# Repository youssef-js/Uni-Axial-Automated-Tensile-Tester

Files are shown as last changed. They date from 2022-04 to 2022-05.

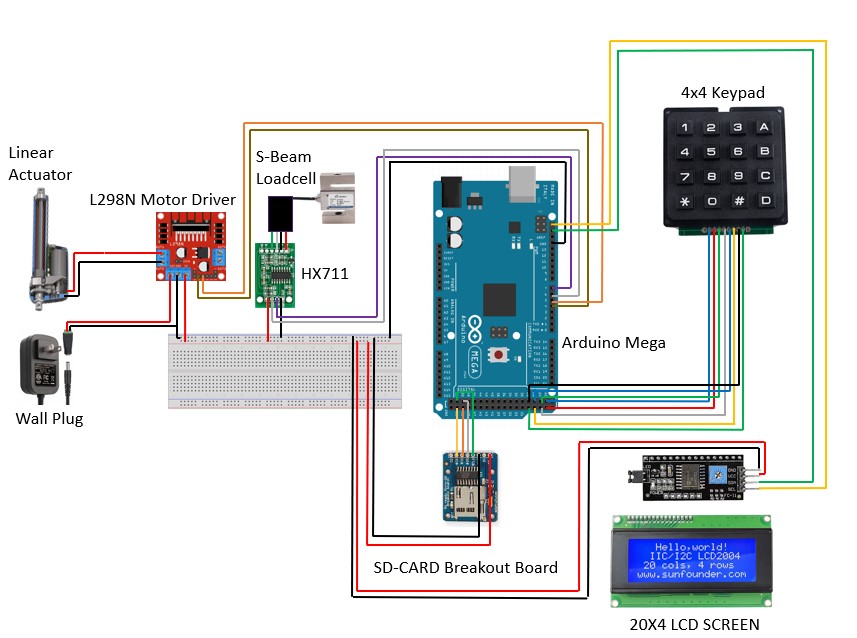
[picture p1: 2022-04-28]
Misc/Circuit Schematic.jpg

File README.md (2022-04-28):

# Uni-Axial Automated Tensile Tester
 ECE 442 Systems Analysis and Design Final Project
 
 The University at Albany’s chemistry department, as part of their educational mission, intends to build a laboratory for undergraduate students where they can gain hands on experience testing various material properties (including tensile strength).  However, due to the extremely high cost of commercial products they have been unable to equip such a laboratory.  

The goal of this project is to build an accurate, low cost, easy to use uniaxial tensile strength tester to support this educational mission. 

 ### Repository Contents
 
 In the interest of transparency all project reports have been included. Reading through this documentation will provide an individual with information on key milestones that were achieved during the progressive evolution of the product. Specifically the "Reports" folder contains the following: 
 
 * Logical Design Report
 * Physical Design Report
 * Experimental Results Report 

 Furthermore, within the "Presentations" folder viewers have been provided with a final copy of the poster displayed at the undergraduate research conference. As well as the presentation slides utilized within the classroom setting that exemplify the accomplished work within a condensed format.

 Lastly, in the scenario were an individual may wish to replicate the design we have provided the source code that is used to control the logic behind the device. Stl files have also been included, these can be found within the "Misc" folder. When printed the 3D models will yield the following:
 
 * Clamps
 * LCD Case
 * Keypad Case

Moreover, within the same folder will be a link to a webpage that will contain an appropriate training guide and more information on the apparatus.
 
  ### System Parts
  
  The system was designed with the intention of being completely reproducible by any individual with the desire to do so. As such for the convenience of the prospective designer, the utilized components and their respective links are compiled below:
  
  1. Drive System

     * Eco-Worthy 300mm Stroke Linear Actuator
  
       Link: https://www.amazon.com/dp/B00NM8H5SW?ref=ppx_yo2ov_dt_b_product_details&th=1
       
     * L298N Motor Driver
  
       Link: https://www.amazon.com/dp/B014KMHSW6?psc=1&ref=ppx_yo2ov_dt_b_product_details
      
     * Wall Mounted AC to DC Adapter
  
       Link: https://www.amazon.com/dp/B087NPBC1W?ref=ppx_yo2ov_dt_b_product_details&th=1
    
  2. User Interface
  
     * 20x4 LCD Display
  
       Link: https://www.amazon.com/dp/B08V4WB3Y1?ref=ppx_yo2ov_dt_b_product_details&th=1
       
     * 4x4 Matrix Keypad 
  
       Link: https://www.adafruit.com/product/3844?gclid=Cj0KCQjw06OTBhC_ARIsAAU1yOWN-53pa0KvsjR3zv9O0FhG5_UUUdQQNal-UVi3GDCMKE0uApMlhS8aAhVsEALw_wcB
      
     * Adafruit MicroSD Card Breakout Board
  
       Link: https://www.amazon.com/dp/B00NAY2NAI?psc=1&ref=ppx_yo2ov_dt_b_product_details
  
  3. Data Collection
  
     * HX711 Load Cell Amplifier
  
       Link: https://www.amazon.com/dp/B07MTYT95R?psc=1&ref=ppx_yo2ov_dt_b_product_details
       
     * S-type Beam High-Precision Load Cell
  
       Link: https://www.amazon.com/gp/product/B0785MXVYK/ref=ppx_yo_dt_b_asin_title_o00_s00?ie=UTF8&psc=1
       
     * Arduino Mega 
  
       Link: https://www.amazon.com/ELEGOO-ATmega2560-ATMEGA16U2-Projects-Compliant/dp/B01H4ZDYCE/ref=asc_df_B01H4ZLZLQ/?tag=hyprod20&linkCode=df0&hvadid=309743296044&hvpos=&hvnetw=g&hvrand=5459596528536033104&hvpone=&hvptwo=&hvqmt=&hvdev=c&hvdvcmdl=&hvlocint=&hvlocphy=9004731&hvtargid=pla-490931309987&th=1
       
  4. Store-Bought Components
  
     * Wood, Wood Screws, L Brackets, Magnets, Assorted Bolts/Nuts/Washers. 
  
       Store: Lowes
       
     * Load Cell Bolts
  
       Store: ACE Hardware

 ### Itemized Expenses
  
| Category      | Item          | Price |
| ------------- |:-------------:| -----:|
| Drive System  |Linear Actuator|$42.99 |
|               |L298N Driver   | $6.99 |
|               | AC-DC Adapter | $7.98 |
|               |               |       |
| User Interface| 20x4 LCD      | $6.33 |
|               | 4x4 Keypad    | $5.95 |
|               |MicroSD Board  | $9.56 |
|               |               |       |
|Data Collection|HX711 Amplifier| $1.99 |
|               |Load Cell      |$51.91 |
|               |               |       |
|Store-Bought   |All-Inclusive  |$30.00 |
|               |               |       |
|Grand Total    |-------------  |$163.70|

**Arduino Mega cost not included, the microcontroller was provided to the class by the instructor and therefore does not qualify as an expense.

   ### Software Dependencies
   
   In the context of software dependencies there is none for the traditional user. This apparatus requires no external downloads and is advertised as a complete stand-alone product due to the microSD functionality allowing for an individual to interact with data from the device in the form of a txt file. As such, appropriate data analysis can be performed at the users discretion, it is anticipated that for chemistry students excel will be the preferred tool.
   
However, when initially setting up the device one must upload the source code onto the microcontroller. The first step is to download the Arduino IDE, the appropriate link is found below:

Link: https://www.arduino.cc/en/software

Next, it is important that the required libraries for the provided Arduino source code are properly configured. The procedure for doing so is concisely formatted below:

   Utilize Link --> Press "Code" Button --> Download the ZIP --> Extract files into the "libraries" folder for Arduino.

   -HX711_ADC Library
   
   Link: https://github.com/olkal/HX711_ADC
   
   -LiquidCrystal_I2C Library
  
   Link: https://github.com/johnrickman/LiquidCrystal_I2C
   
   -Keypad Library
  
   Link: https://github.com/Chris--A/Keypad
   
   -EEPROM Library
  
   Link: N/A (Built into Arduino IDE)
   
   -Wire Library
  
   Link: N/A (Built into Arduino IDE)
   
   -SD and SPI Library
  
   Link: N/A (Built into Arduino IDE)

Syntax to reference libraries:

(Provided for the readers understanding, these lines of code have already been included within the source code and there is no need for the user to make any additions.)
```C
// Load cell
#include <HX711_ADC.h>
#include <EEPROM.h>

// LCD
#include <Wire.h>
#include <LiquidCrystal_I2C.h>

// Keypad
#include <Keypad.h>

// SD Card
#include <SD.h>
#include <SPI.h>
```

At this stage the setup in terms of software has been completed. Please download the source code provided within this repository and upload to the microcontroller to begin using the apparatus.

### Personnel and Funding

This project is completely funded by the Center For Undergraduate Research And Creative Engagement (CURCE). The designers applied for a $500 award and were subsequently granted the sum after passing the validation process. 

Designers

1. Youssef Jalwaj Soubai

2. Mazin Chater

3. Jaden Pharoah

Faculty Mentors/Support

1. Jonathan Muckell

2. Mike Denmark

Special thanks to Professor Chen, Feldblyun, Yeung, and the University at Albany’s Chemistry Department for sponsoring this project. 

Developed in ECE442: Systems Analysis & Design in the Electrical & Computer Engineering Department.

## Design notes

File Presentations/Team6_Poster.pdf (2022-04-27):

# Uni-Axial Automated Tensile System

# Youssef Jalwaj Soubai, Mazin Chater, Jaden Pharoah

## Department of Electrical & Computer Engineering, University at Albany

## Problem Statement

- The University at Albany’s chemistry department, as part of their educational mission, intends to build a laboratory for undergraduate students where they can gain hands on experience testing various material properties (including tensile strength). However, due to the extremely high cost of commercial products they have been unable to equip such a laboratory.
- The goal of this project is to build an accurate, low cost, easy to use uniaxial tensile strength tester to support this educational mission.

## System Requirements

## Experimental Results

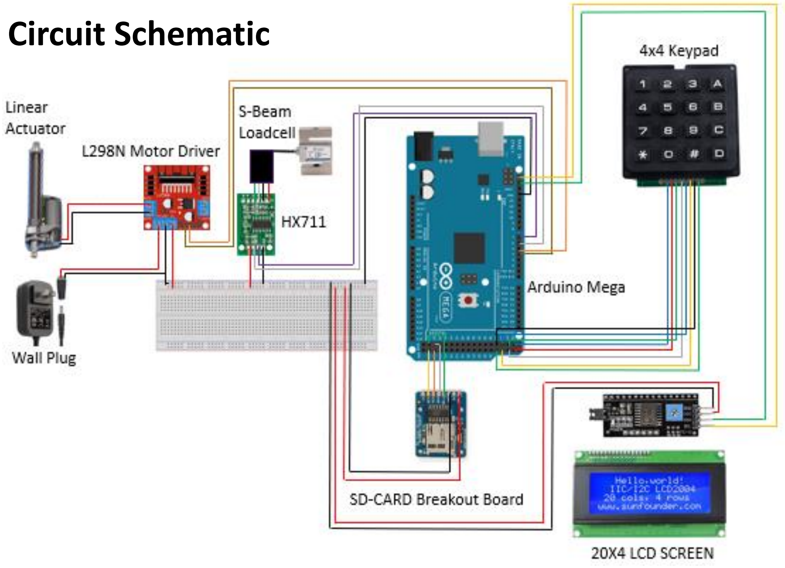
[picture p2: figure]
Circuit Schematic

## Project Partners

## System Design

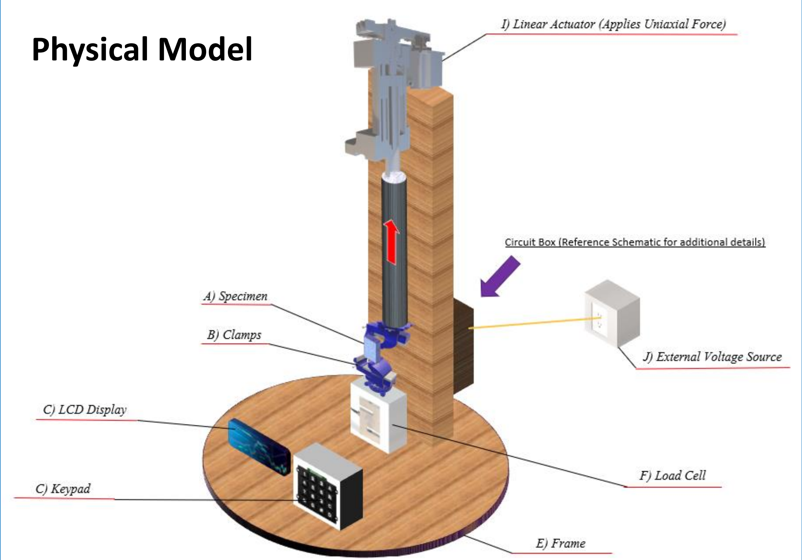
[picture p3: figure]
Physical Model

## System Enhancement Budget

Metric | Sample | Our System | Known Value
Young’s Modulus | Latex | 770 ± 30 kPa | 740 ± 10 kPa
… | Nitrile | 2.4 ± 0.2 MPa | 2.4 ± 0.2 MPa
Ult. Tensile Strength | Latex | 2.7 ± 0.3 MPa | 3.3 ± 0.1 MPa
… | Nitrile | 4.4 ± 0.4 MPa | 4.4 ± 0.1 MPa
Part | Purpose | Cost
50kg Load Cell | Measures Force | $50
Actuator System | Provides uniaxial force | $60
LCD, Keypad, SD | For stand-alone system | $30
Clamp Hardware | Combine 3-D printed parts | $10
TOTAL | | $150

## System Accuracy

- System Accuracy: The system should be able to accurately measure the stress-strain curve, such that Young’s Modulus and Ultimate Tensile Strength can be calculated to within two significant figures.
- System Ease-of-Use: The system should be easy to calibrate and operate by undergraduate students without requiring knowledge of electronics or software programming.

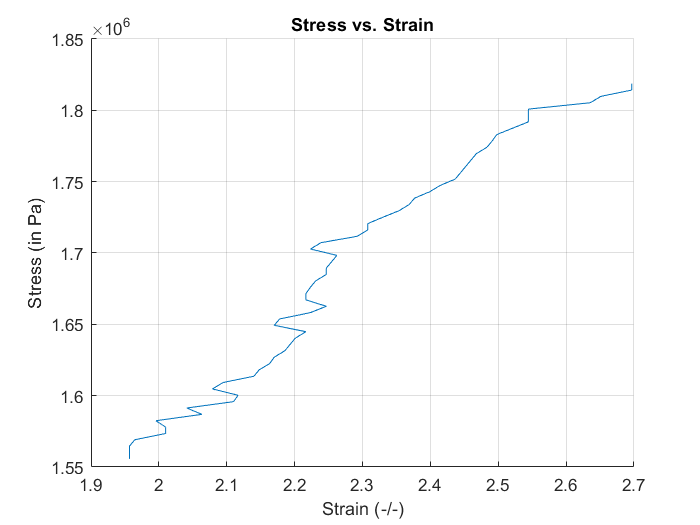
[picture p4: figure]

Figure 1: Original system data. The plot is filled with erroneous content.

## Key System Features

- Uniaxial Drive System - Composed of a L298N DC Motor Driver Module and an Eco-Worthy 300mm Stroke Linear
Actuator. Eliminates the risk of erroneous data due to friction.
- Stand-Alone Apparatus - The incorporation of an LCD screen, keypad, SD card capability and wall plug functionality allows for an independent system. Users can communicate with the device without any added software, thereby emphasizing the practicality of the device.
- Special thanks for Professor Chen, Feldblyun, Yeung, and the University at Albany’s Chemistry Department for sponsoring this project.
- This project was developed in ECE442: Systems Analysis & Design in the Electrical & Computer Engineering Department.

## Signature

## Initial vs. Current Stress/Strain Curves

# Team 6

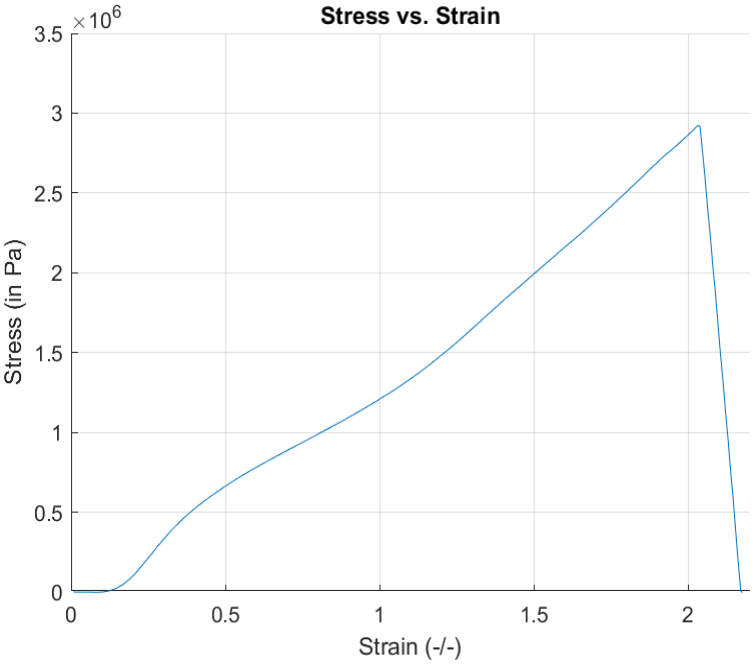
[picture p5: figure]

Figure 2: Data collected from improved system (current implementation). The plot is significantly improved, highlighting the importance of a drive system that applies uniform force.

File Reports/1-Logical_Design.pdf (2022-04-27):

PP-2017 V2.1

ANALYSIS & LOGICAL DESIGN | 1

# Logical Design Proposal Improved Tensile Tester Team 6

Mazin Chater, Youssef Jalwaj-Soubai, Jaden Pharoah

Activity Report

Abstract—A uni-axial tensile tester is a widely used system for gathering ultimate tensile strength and Young’s Modulus of a given material. Generally, these systems can be expensive and sophisticated yet their value as an educational tool for chemistry students is significant. As such, a cheaper, student-friendly design is highly desirable. Provided a minimally functional base model with issues ranging from largely inaccurate and imprecise results, obscure functionality, and generally an unpleasant and non-intuitive user interface, a targeted solution must aim to re-envision and harmonize the old structure into a more refined prototype. What follows is an advanced design that rectifies a number of defects as well as markedly improves accuracy and reliability. Additional ease-of-use features are implemented with an emphasis towards student use. The new capabilities deliver a low-budget, discernibly innovative solution with supporting documentation that sum to provide an accessible educational tool for students.

Index Terms—Uniaxial Tensiometer, System Analysis, Engineering Design

✦

### 1 BACKGROUND

T
ENSILE testers are instruments crucial in the study of materials science. A vast majority of those on the market, however, are thousands of dollars for a single unit and can be overly sophisticated beyond the scope of educational benefit. An alternative solution has been designed with these limitations in mind – one that is fundamentally simplistic with student use considered at its core [1]. The existing solution, nevertheless, has extensive flaws that hinder at the overall goals of reliability, accuracy, and accessibility. Most prominently, the accuracy of the system is only within an order of magnitude of accepted values which is due to a variety of factors including friction losses and unnecessary parts which add
- Mazin Chater,
E-mail: mchater3@albany.edu,
- Youssef Jalwaj-Soubai,
E-mail: yjalwaj-soubai@albany.edu,
- Jaden Pharoah,
E-mail: jpharoah@albany.edu, University at Albany.

to erroneous load cell readings. Ease-of-use is also obstructed with the provided plastic clamps which are especially time-consuming and inconsistent when holding materials. Likewise, data transfer must be performed manually from an Arduino interface to a MATLAB file to generate a stress-strain curve, creating a troublesome barrier for prospective chemistry students. In the purest sense, the following design resolves these issues by bridging the gap between a thought experiment and a fullyfunctional system.

### 2 SYSTEM REQUIREMENTS & CON-

STRAINTS

It’s important to define functional requirements of the system as outlined by both stakeholders and end users. At the forefront of the design must be accuracy and reliability. Having accurate results is only as useful as their consistency and having precisely inaccurate results is similarly of little utility. The constructed design aims to minimize error as well as to

Activity Report

2 | ANALYSIS & LOGICAL DESIGN

maximize reproducible trials. Another key aspect lies in the accessibility of the system. A
functional model is only worthwhile to those
who are capable its operation; therefore, there is merit in recognizing that additional software requirements, a non-intuitive structure and an intimidating arrangement of circuitry among other things are undesirable features to be mitigated. The following requirements describe functionality from a user’s perspective in ideal and alternative scenarios.

### 2.1 Accuracy and Precision

Accuracy is the characteristic that defines the adherence of a measure to a known value, whereas precision refers to the consistency of a measure across multiple iterations. Both qualities are integral to the stakeholder and a functional instrument must contain these attributes. Users engage with the apparatus to test a sample material. Interaction with the system must first consist of calibrating both the load and distance sensor. An LCD screen will guide the user through the process and prompt the participant to input appropriate values such as that of a sample mass or distance. Utilizing this data the sensors will be configured accordingly as to eliminate erroneous outputs. Furthermore, in order to ensure the quality of the load sensor data a more sophisticated load cell has been implemented to maximize the accuracy of measurements. In contrast, the current range sensor has proven to be dependable and is unlikely to be replaced.
Normal Flow
- Step #1: Initiate calibration process via button press.
- Step #2: Enter sample mass or distance value when prompted.
- Step #3: Instate the sample condition.
- Step #4: Confirm step via button press.
- Step #5: Repeat steps 2-4 until confirmation message is displayed.
- Step #6: Proceed with experiment. Alternative Flow This describes what will happen under an error condition.
- Step #1: Error message will display citing imprecise measurements.
- Step #2: User will be unable to proceed under erroneous conditions.
- Step #3: LCD Screen will prompt the user to initiate the calibration process once again.

### 2.2 Accessibility

Having an accurate and reliable system is significant, but the system must be functional for its intended audience. To make the system accessible, design elements shall consider the stakeholders’ experience and goals when interacting with the model and prioritize elements that maximize fluidity. An LCD screen in addition to its value as a calibration mechanism is also inherently user-friendly by providing simple options that hide the complex operations behind them. Users will merely select an option (i.e. start test, end test, send data, etc) and can disregard background intricacies. Modified clamps similarly serve to minimize setup time by dispensing with unnecessary screws and by implementing a simpler method whereby the clamps may open. Users will open each clamp with a single knob and firmly place the material in a matter of seconds, allowing for more tests to be conducted and minimizing hassle associated with the base model. Normal Flow
- Step #1: Place a sample firmly between both clamps.
- Step #2: Use the LCD screen to select the Start Test option.
- Step #3: Upon the sample tearing, select the End Test option.
- Step #4: Select the Send Data option.
- Step #5: Receive the data via network connection.
Alternative Flow This describes what will happen under an error condition.
- Step #1: Select the Refresh System option on the LCD screen.
- Step #2: Once reloaded, follow normal case steps.
- Step #3: If error persists, re-upload code using Arduino software as specified in the system documentation.

PP-2017 V2.1

SURNAME et al. | 3

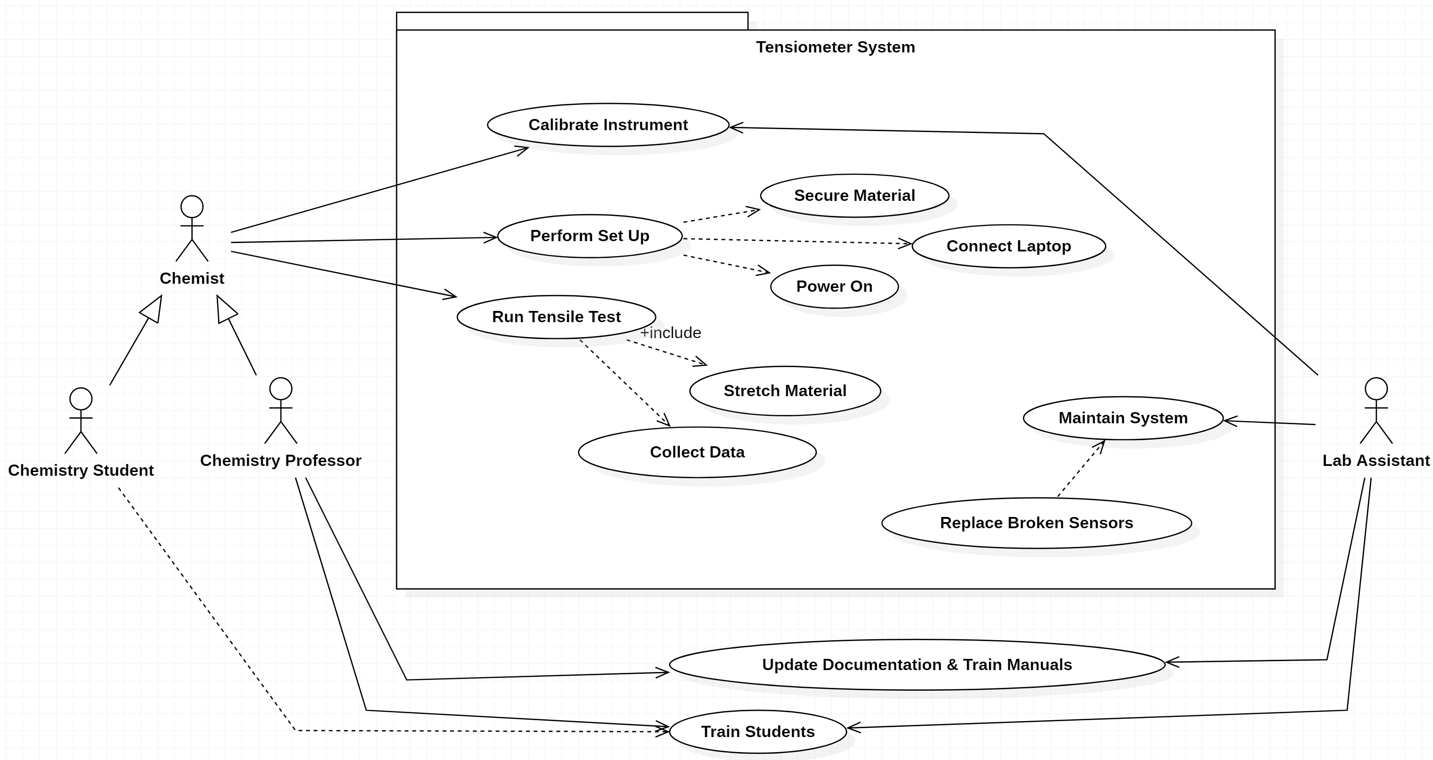
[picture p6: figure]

Figure 1. Use case model of the tensiometer system depicting system actors and the desired actions the system is required to support.

### 2.3 Constraints

The stakeholders have imposed certain restrictions upon the design process. System constraints are defined below and detail the conditions that the resulting testing apparatus must abide by.

- Time Constraint: Completed and ready to presentation/demonstrate by April 22nd
- Budget: Cost needs to be below $150. Exceeding the budget will require strong justification as to the value added from the cost overrun.
- Replication: Relatively straight-forward process to replicate project work, such that an individual can build out a lab of identical tensiometers.
- Accessibility of Parts: Parts need to be readily accessible, ship quickly (not on back order) and available from common part suppliers (e.g., Digikey, Mouser, Adafruit, SparkFun, Amazon). Parts that are difficult to source should be avoided.
- Safety: System must be safe to operate without significant training or supervision

### 3 LOGICAL DESIGN

The proposed design is simplistic in nature and abides by all given constraints. A visual depiction of the logical design is detailed within Figure 2. Referencing this image an individual first takes notice of the structural frame. A combination of wood and metal rods the testing apparatus lies upon a sturdy foundation. The drive system is comprised of a linear actuator that applies the necessary uni-axial force. The bottom clamp is attached to the end of the actuator, whereas the top clamp is fastened to the load cell. Our specimen of interest will be placed between these entities. Data will be collected from both the load cell and range finder. This information will be read by the micro-controller, processed accordingly and sent to the LCD display. Furthermore, if the user desires they may export the test data to their personal machine via network connection.

### 3.1 Design Justification

The proposed design is superior to potential alternatives due to a myriad of factors. Specifically, the selected design is an entirely stand

Activity Report

4 | ANALYSIS & LOGICAL DESIGN

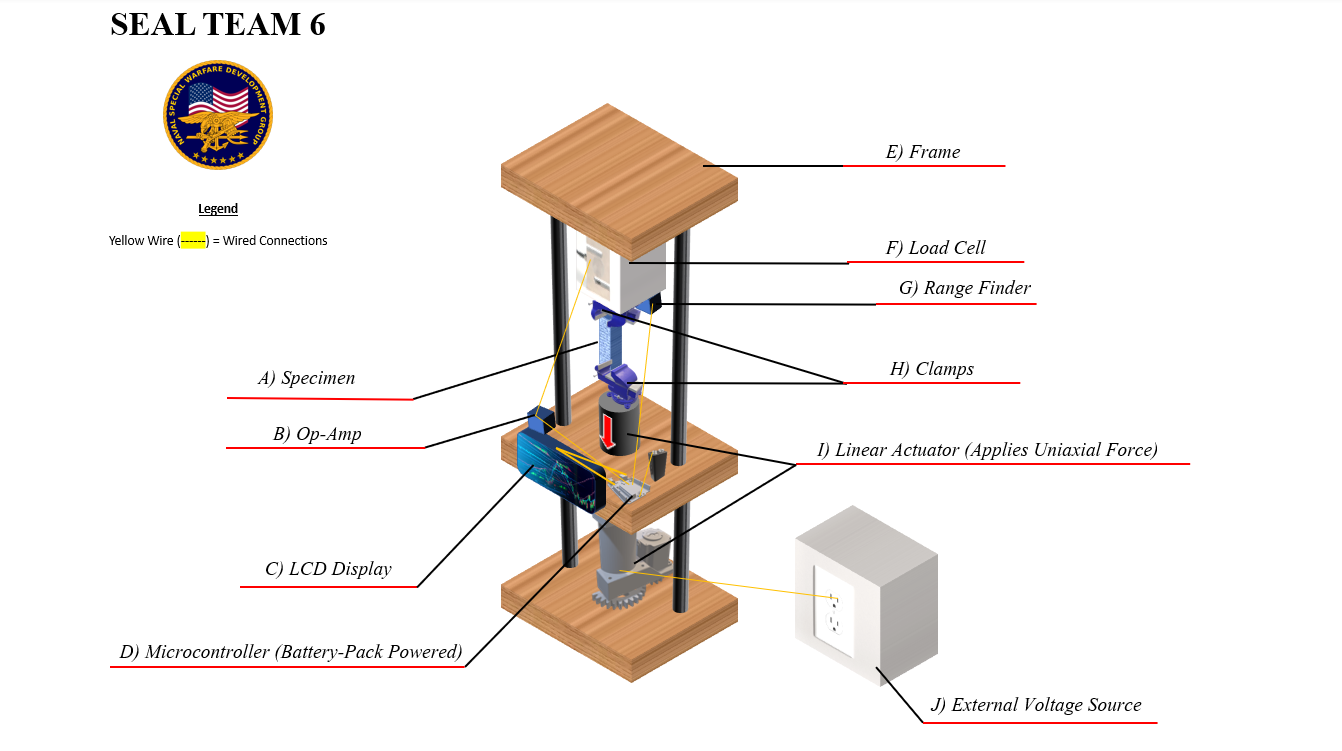
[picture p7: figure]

Figure 2. Logical prototype of the current system. Of key importance is the uni-directional movement of the clamps and addition of an interactive LCD screen as a user interface.

alone apparatus and does not require the user
to own a laptop. Removing such dependencies
denotes that all students will be able to participate within a lab regardless of preparation. Furthermore, the device is ergonomically sound, this denotes that even an individual with no prior experience may perform a successful tensile test. The entire process is iteratively walked through via clear instructions presented on the LCD screen. Moreover, the selected drive system allows for a constant and reliable form of force application. Utilizing the linear actuator a user will have far more consistent results compared to a manual system such as a handcrank. The referenced implementations sum to unveil a working mechanism that satisfies client requirements quite comfortably.

REFERENCES

[1] J. H. Arrizabalaga, A. D. Simmons, and M. U. Nollert, “Fabrication of an economical arduino-based uniaxial tensile tester,” Journal of Chemical Education, vol. 94, no. 4, pp. 530–533, 2017. [Online]. Available: https: //doi.org/10.1021/acs.jchemed.6b00639

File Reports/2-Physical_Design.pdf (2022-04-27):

PP-2017 V2.1

PHYSICAL DESIGN | 1

# Physical Design Proposal Seal Team 6

Mazin Chater, Youssef Jalwaj-Soubai, Jaden Pharoah

Activity Report

✦

### 1 PROPOSED SOLUTION

Targeting a significant increase in accuracy and precision along with an accessible architecture, the new system introduces a number of measured improvements. In terms of construction, a sophisticated yet simple clamp design is implemented along with a mounted S-beam load cell capable of greater flexibility in applied force as well as improved accuracy. A linear actuator applies uni-axial force to lift the top clamp upward, eliminating human error and providing uniform data collection. With accessibility in mind, an LCD screen guides users through the calibration and testing, minimizing barriers to entry otherwise prevalent with software. The features collectively combine under a new, custom frame designed for the aforementioned features.

### 2 SYSTEM ARCHITECTURE

A small wooden base holds the foundation for the system with a S-beam load cell being attached to the back center of the wood. Above, the carefully aligned bottom clamp attaches to the top of the load cell. The opposing clamp rests adjacent to the bottom clamp, effectively mirroring about the x-axis. When conducting

- Mazin Chater,
E-mail: mchater3@albany.edu,
- Youssef Jalwaj-Soubai,
E-mail: yjalwaj-soubai@albany.edu,
- Jaden Pharoah,
E-mail: jpharoah@albany.edu, University at Albany.

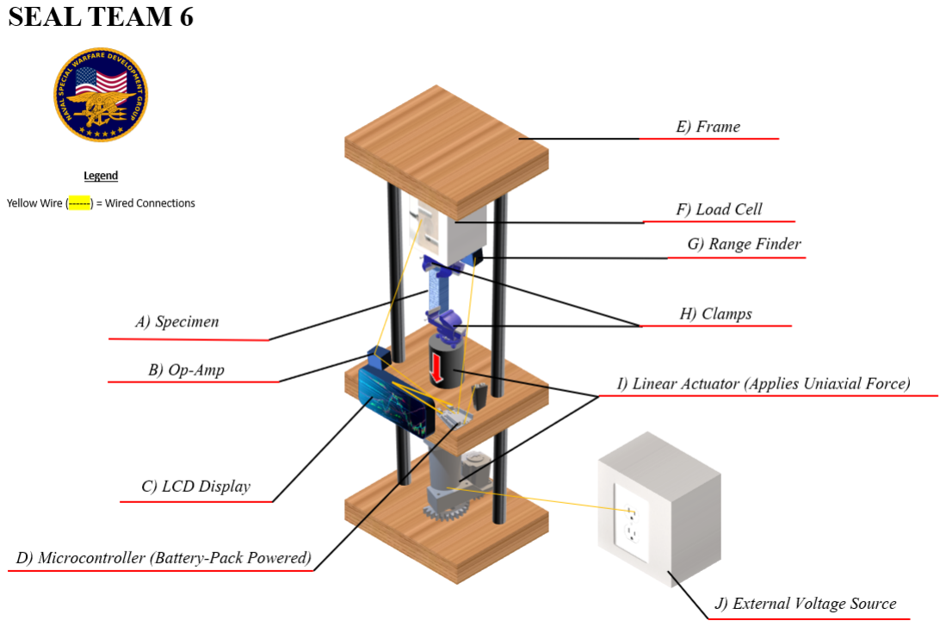
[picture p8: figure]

Figure 1. Prototype physical design model of the tensile strength tester with added features.

a test, the head of the top clamp is pulled upwards by a linear actuator that rests above. Back at the base, an LCD screen with trivial button inputs guides users through calibration, starting and ending tests, and sending collected data to a preferred destination.
A mounted breadboard and Arduino micro-controller connect to the load cell, distance sensor, and linear actuator. Specialized algorithms in a finite state machine are the basis for the design. As seen in Figure 2, the load cell becomes operational through connection to the HX711 board which uses the amplified value to perform a ADC conversion and then communicates the results using the I2C communication standard with the attached micro-controller. The load cell itself uses a wheatstone bridge to detect slight changes in voltage when an applied force is present. Additionally, the HC-SR04 distance sensor calculates distance with a trigger pin that sends a signal and an echo pin

Activity Report

2 | PHYSICAL DESIGN

which receives the signal. The time difference
along with the speed of sound is used to calculate distance. Furthermore, one must discuss
the nucleus of the design, a uniaxial drive system. The current working model incorporates the abilities of a ”L298N DC Motor Driver Module” and that of an ”Eco-Worthy 300mm Stroke Linear Actuator”. Including the L298N component allows for rotational direction control utilizing H-bridge properties. The motor driver also allows a user access to direction control pins that are easily interfaced with the Arduino micro-controller.

### 2.1 System Components

When considering the variety of materials to be tested in the prospective system especially those with higher ultimate tensile strengths, it became apparent that limiting exerted force to 5kg would be insufficient. It was also clear under the previous load-cell model that the application of force could only be done accurately in a precise, impractical environment. As such, a 50kg S-beam load cell has been implemented to vastly expand force possible while simultaneously maintaining accurate readings across extensive design elements. S-beam load cells vary in both cost and mass rating, though generally it should be noted that a number of these variants can be considered appropriate; 20kg, 40kg, and even 100kg are mass ratings that can be potentially utilized for distinct testing purposes. Observe, higher mass ratings yield higher inaccuracies in data readings and thus finding a balance between accuracy and capability should be evaluated.
User accessibility is another design criteria taken with consideration with the addition of an LCD screen interface. A 20x4 LCD screen guides users to navigate between testing phases such as running a test, calibration, and sending resultant data. A low cost LCD screen essentially gives users the ability to bypass complex software interfaces like the Arduino IDE and MATLAB. Rather than choose the somewhat more common 16x2 dimension, a 20x4 screen can print the entire menu concurrently without need for scrolling operations. An attached I2C board also simplifies wiring and congestion on the Arduino micro-controller. To interface with the screen, users interact with a linked membrane keypad implemented to register simple selections as well as recognizing a manual calibration input.
In the context of implementing a uniaxial drive system the available components on the market were rather limited due to the imposed budget cap. Ultimately the ”L298N DC Motor Driver Module” and ”Eco-Worthy 300mm Stroke Linear Actuator” were chosen due to their ease of use and affordability. Furthermore, a unique aspect of the L298N module is that it also powers the Arduino micro-controlller. As such, designers may advertise the final product as an entirely stand-alone system, this notion is a desirable quality that further emphasizes the ergonomic nature of the apparatus. Reference Figure 3 for an overview of incurred costs.

2.1.1 Load Cell (50kg) / HX711 Amplifier Functionality in the load cell effectively mirrors the previous model with enhanced precision, mass range, and accessibility in terms of mounting.

2.1.2 Ultrasonic Range Sensor
Preexisting in base model; see previous documentation.

2.1.3 Micro-controller
Preexisting in base model; see previous documentation.

2.1.4 Graphical Display
The new system gives users a membrane keypad to interact with a 20x4 LCD interface whereby navigation moves across four different states: menu, run test, calibration, and send data.

2.1.5 Uniaxial Drive System
Composed of a L298N DC Motor Driver Module and an Eco-Worthy 300mm Stroke Linear Actuator. The motor driver employs the use of an H-bridge to allow for direct control over rotational direction. Moreover users have access to input pins, this allows for seamless automation given an appropriate script.

PP-2017 V2.1

SURNAME et al. | 3

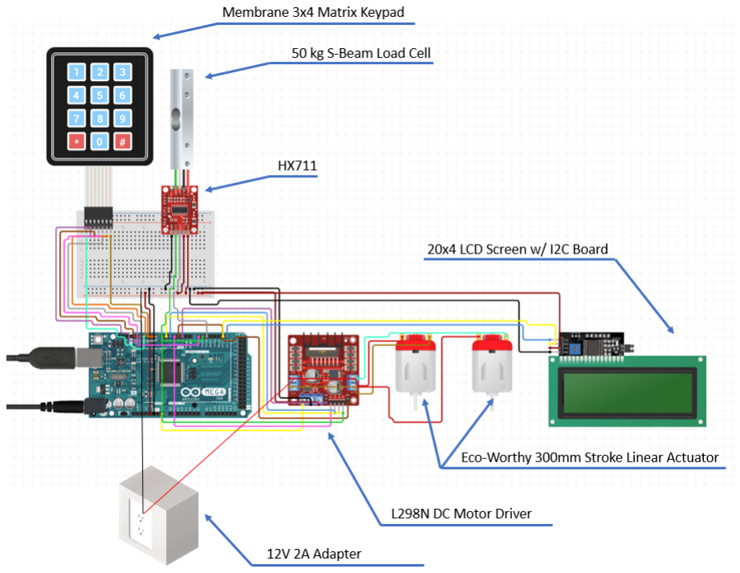
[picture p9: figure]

Figure 2. Schematic diagram of tensiometer electronics with additional actuator, LCD screen, and membrane keypad.

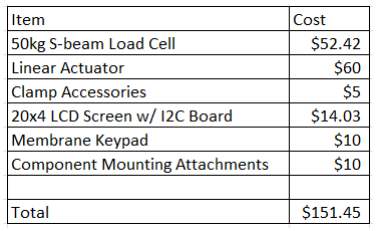
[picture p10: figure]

Figure 3. Parts purchased and their respective costs.

### 2.2 Engineering Standards

Engineering standards establish technical criteria, methods, processes and practices. In the current system, there are two communication standards (protocols) that are utilized: I2C and UART.

2.2.1 I2C Protocol
I2C supports multiple controllers and peripherals using just two wires (data and clock). In any new communication sequence, the address frame of 7 bits is always first followed by the ACK/NACK bit which gives confirmation that each frame is transferred successfully. Limited to 8 bits, the data frame begins transmitting data as the controller continues generating

Activity Report

4 | PHYSICAL DESIGN

clock pulses at a regular interval and the data
is placed on SDA by either the controller or
the peripheral. Once all the data frames have
been sent, the controller will generate a stop condition.

2.2.2 UART Protocol
UART ports communicate between only two devices (transmit and receive). Both devices must agree on data and communication speed ahead of time and requires complex hardware. There is no control over when the data is sent and no guarantee that both sides are running at the same rate. To achieve reduced data rates, at least one start and stop bit is a part of each frame of data.

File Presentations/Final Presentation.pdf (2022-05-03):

# Automated

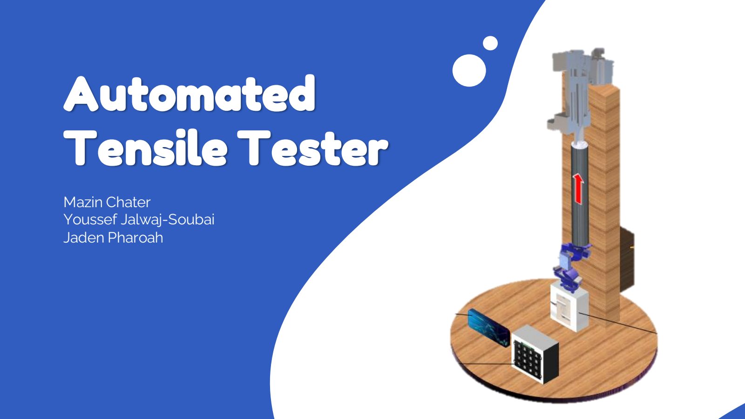
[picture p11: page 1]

# Tensile Tester

Mazin Chater
Youssef Jalwaj-Soubai
Jaden Pharoah

# Overview

Summary of system
functionality

## Abstract

How requirements
influenced the design

## System Features

Cost of individual
components

## Budget

A guide for prospective
users

## Website

Live test results &
discussion

## Data

Time to answer any
questions

Q/A

01

04

02

05

03

06

# Abstract

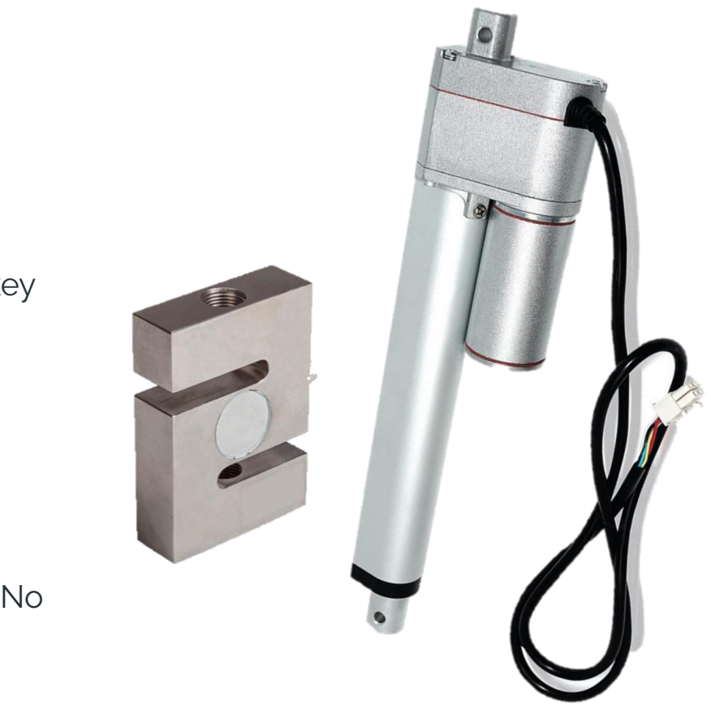
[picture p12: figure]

Our design revolves around these key design aspects:

- Linear actuator
- S-beam load cell
- LCD & keypad
- SD card

The system is entirely stand-alone. No software or laptop is required.

# System Requirements

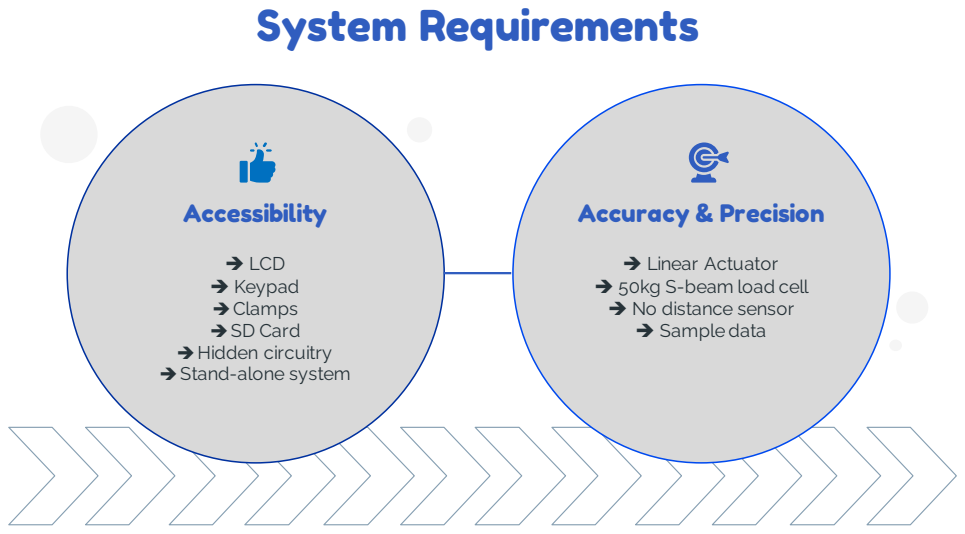
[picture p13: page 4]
Accessibility; Accuracy & Precision

➔ LCD
➔ Keypad
➔Clamps
➔SD Card
➔Hidden circuitry
➔Stand-alone system

➔ Linear Actuator
➔ 50kg S-beam load cell
➔ No distance sensor
➔ Sample data

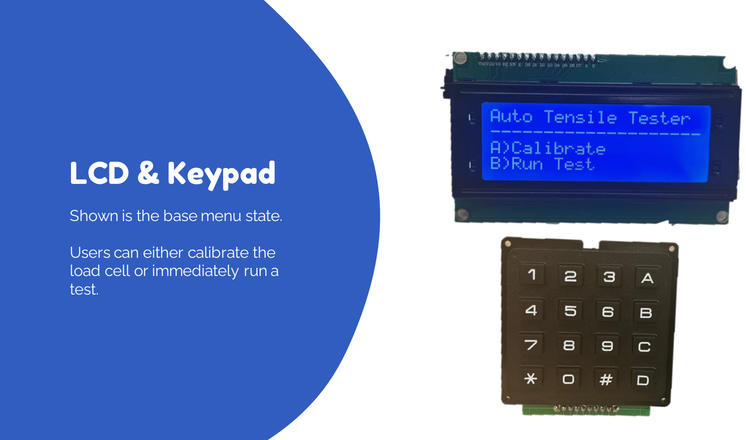
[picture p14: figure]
LCD & Keypad; Shown is the base menu state.; Users can either calibrate the load cell or immediately run a test.

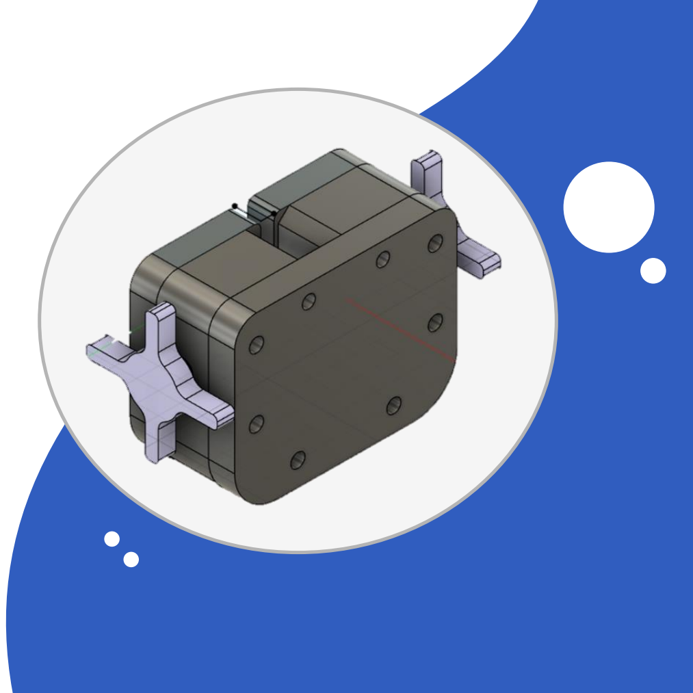
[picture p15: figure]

# Clamps

Strong grip clamps provide easy material placement and uniform sample strain.

Users mount the material in place and return to the LCD interface when ready.

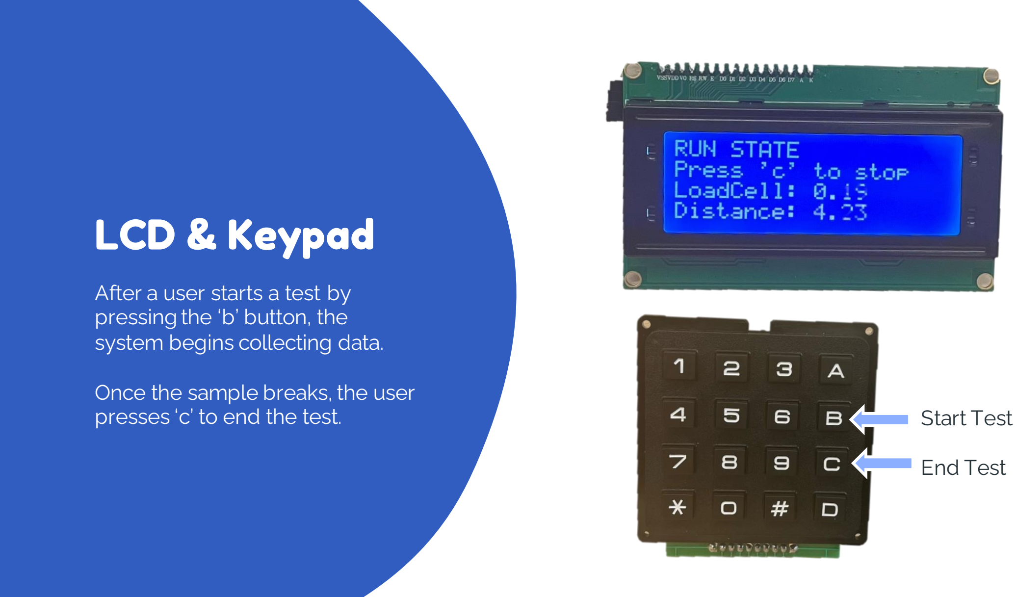
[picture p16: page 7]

# LCD & Keypad

After a user starts a test by pressing the ‘b’ button, the
system begins collecting data.

Once the sample breaks, the user
presses ‘c’ to end the test. | Start Test
| End Test

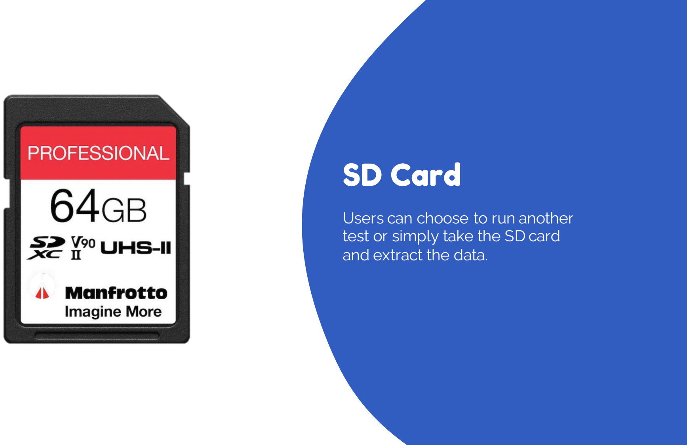
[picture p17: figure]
SD Card; Users can choose to run another test or simply take the SD card and extract the data.

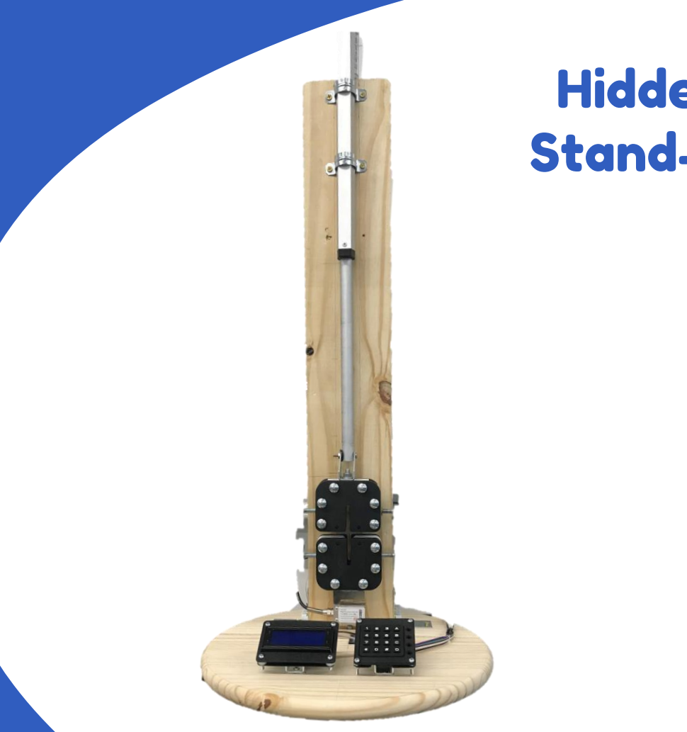
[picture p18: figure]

# Hidden Circuitry & Stand-Alone System

No specific software necessary. No laptop required.
→ Simply plug-in and start collecting data.

Essentially all wires are hidden on the backside of the system.

Users simply see the LCD and keypad interface along with the sample stretching.

# Accuracy & Precision

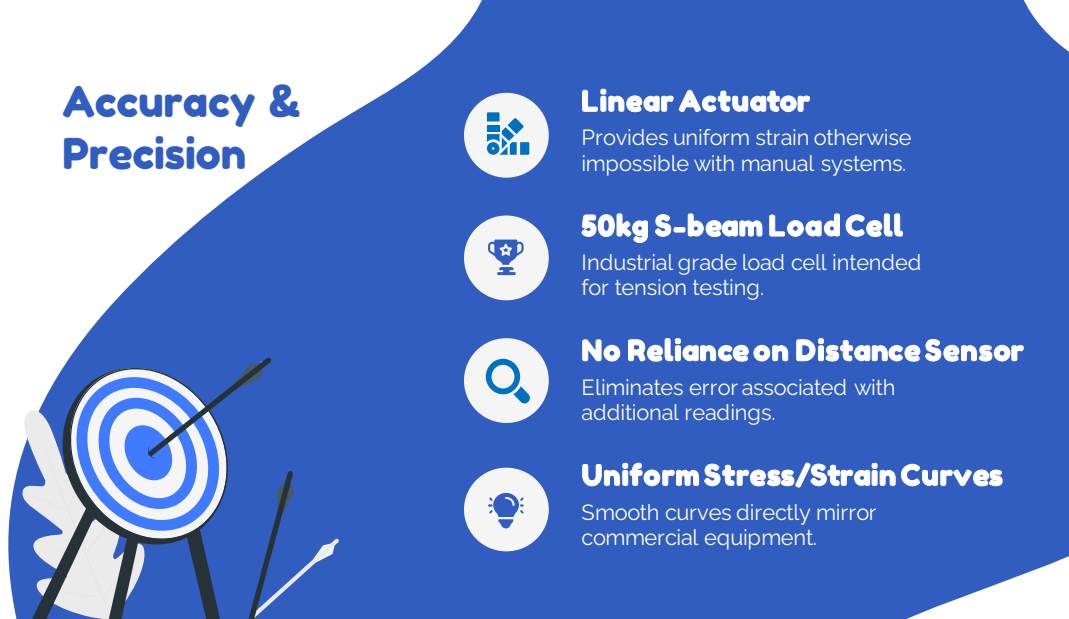
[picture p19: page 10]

Linear Actuator
Provides uniform strain otherwise
impossible with manual systems.
50kg S-beam Load Cell
Industrial grade load cell intended
for tension testing.
No Reliance on Distance Sensor
Eliminates error associated with
additional readings.
Uniform Stress/Strain Curves
Smooth curves directly mirror
commercial equipment.

# Sample Plots: Nitrile

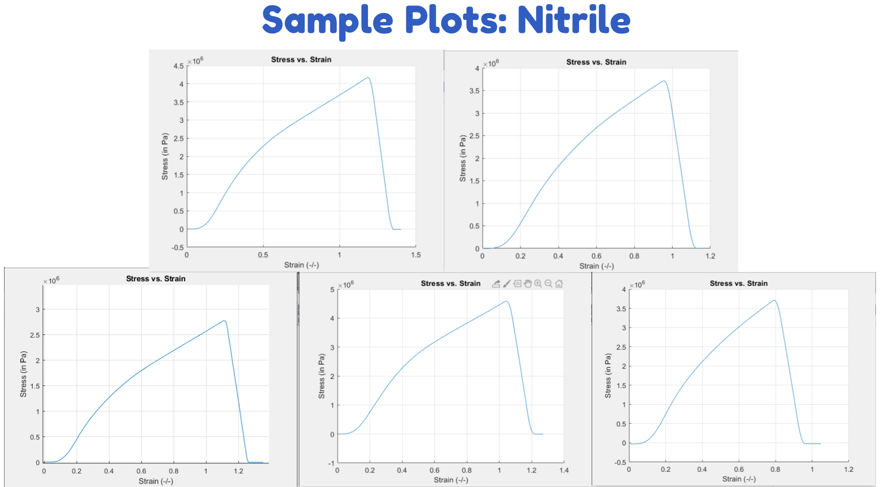
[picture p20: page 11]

# Sample Plots: Latex

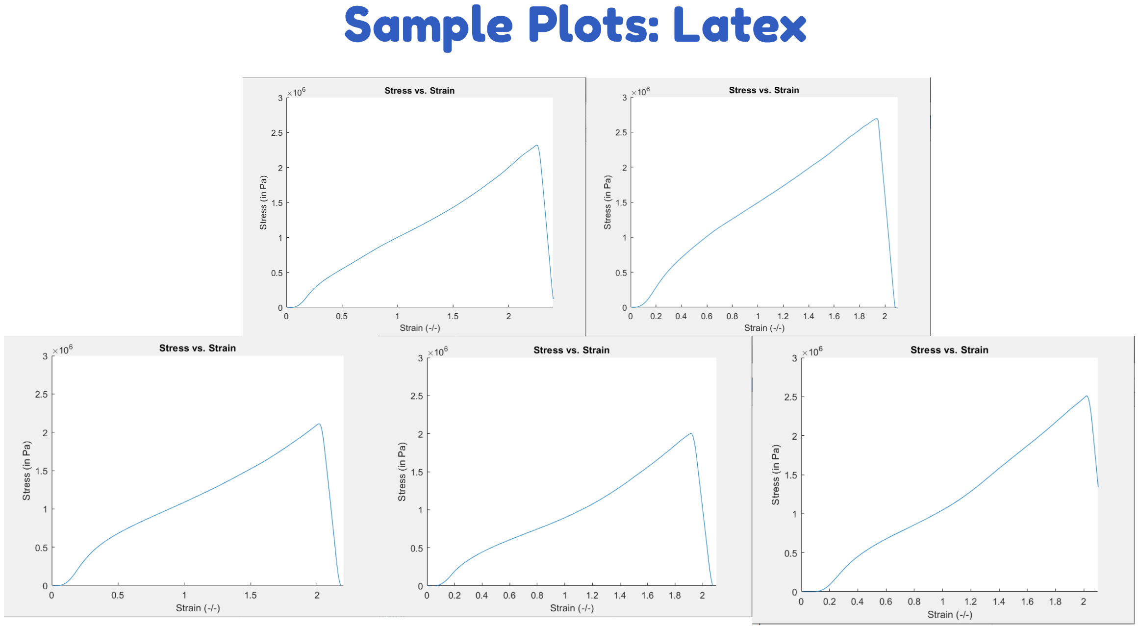
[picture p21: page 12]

# Budget

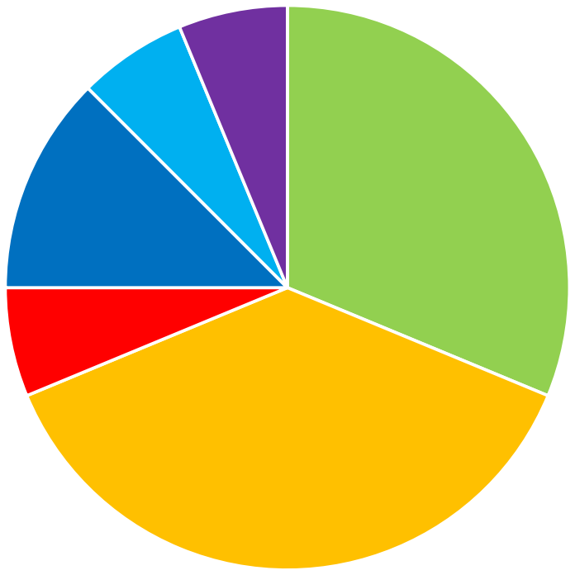
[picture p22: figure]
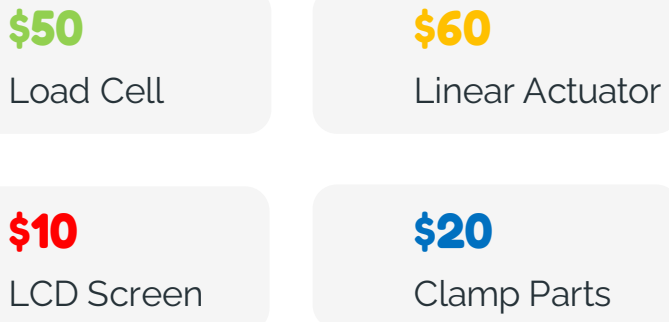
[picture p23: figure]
Clamp Parts; Linear Actuator; LCD Screen; Load Cell

Keypad

$10
SD Card

$10

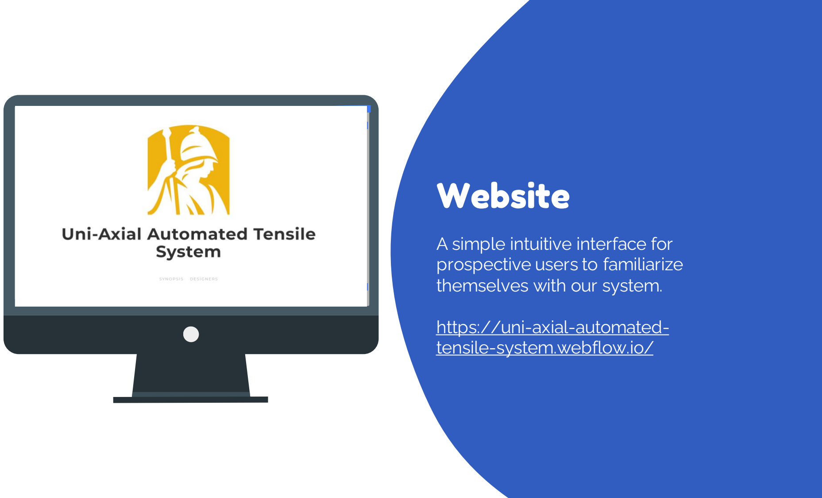
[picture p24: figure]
Website; A simple intuitive interface for prospective users to familiarize themselves with our system.; https://uni-axial-automated- tensile-system.webflow.io/; AUTOMATED TENSILE SYSTEM; Mazin Chater; Youssef Jalwaj Soubai; Jaden Pharoah

# Thank you

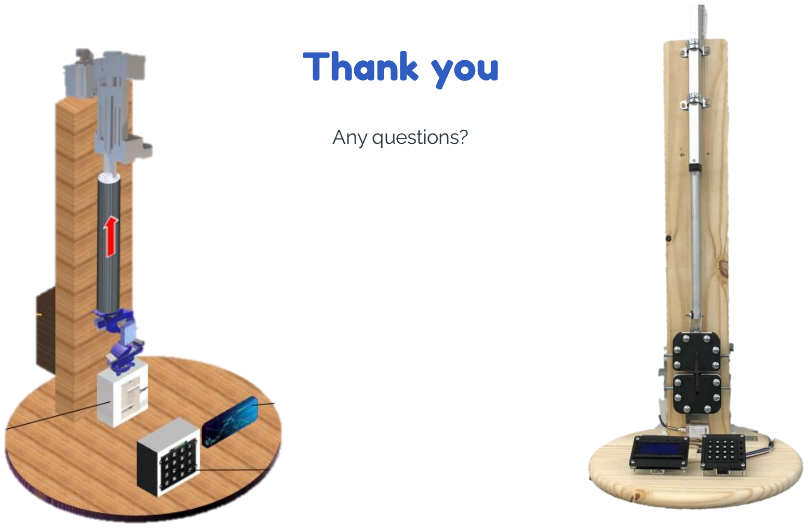
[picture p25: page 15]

Any questions?

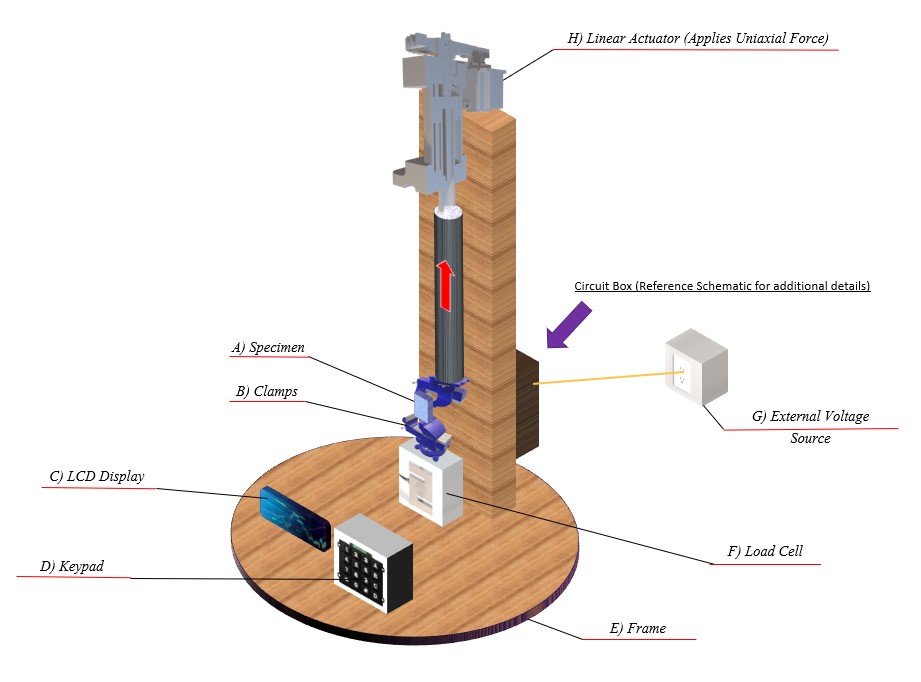
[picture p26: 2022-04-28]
Misc/Physical Model.jpg

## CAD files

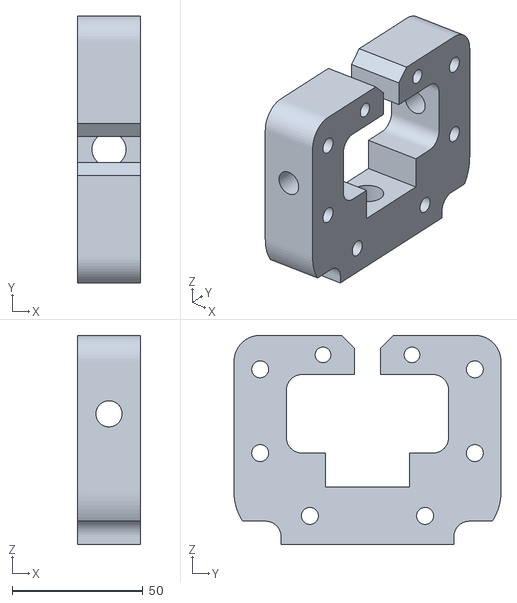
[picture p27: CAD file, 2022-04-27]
Misc/Clamp 3D Model/Central_Piece.stl
24.0 x 102.0 x 80.0

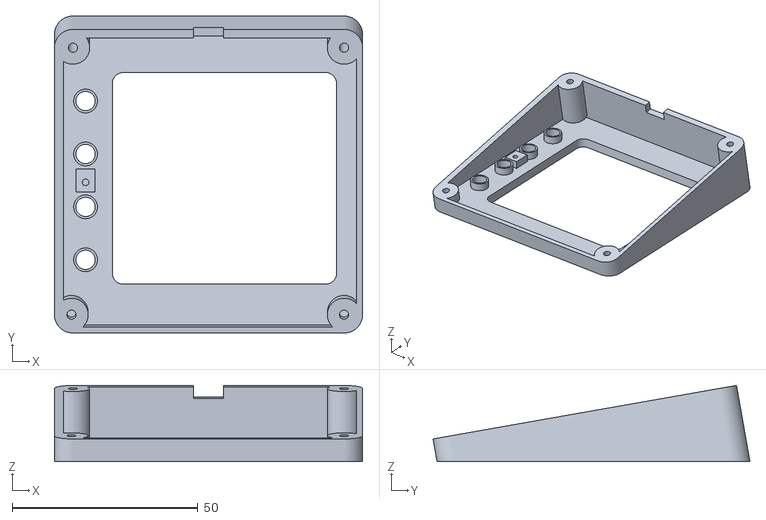
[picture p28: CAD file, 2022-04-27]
Misc/Keypad Case 3D Model/case-top.stl
83.0 x 85.4 x 20.5

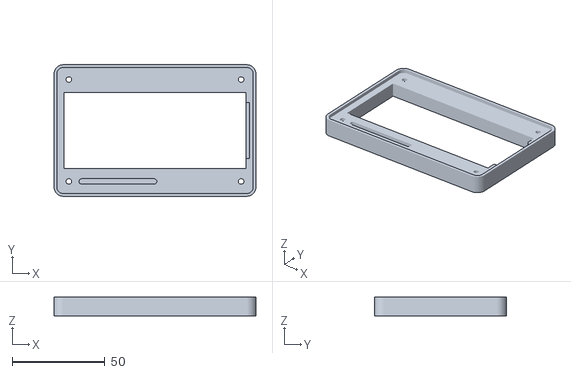
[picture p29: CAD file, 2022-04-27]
Misc/LCD Case 3D Model/20x4Case_TOP.stl
109.0 x 71.0 x 10.0

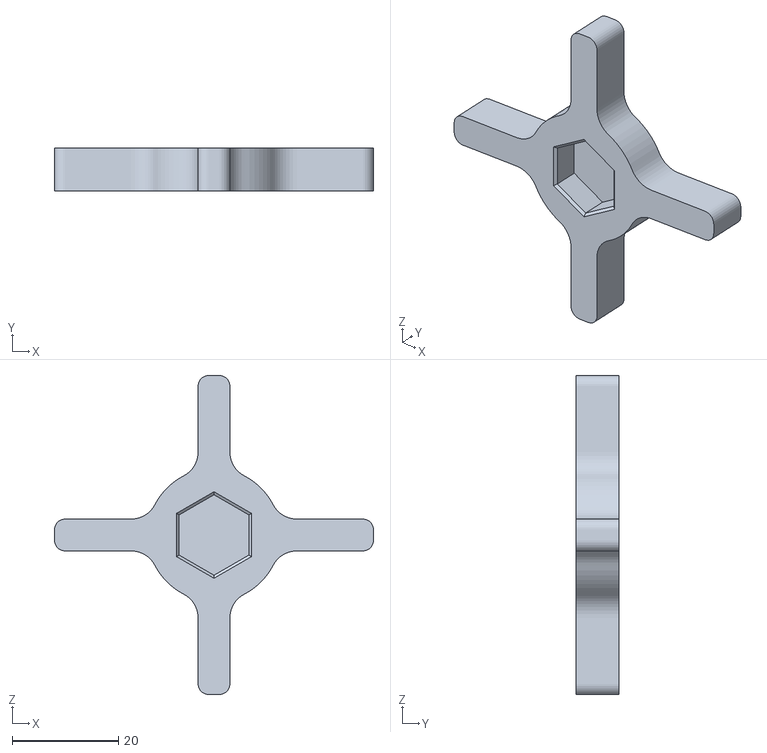
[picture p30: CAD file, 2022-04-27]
Misc/Clamp 3D Model/Knob.stl
60.0 x 8.00 x 60.0

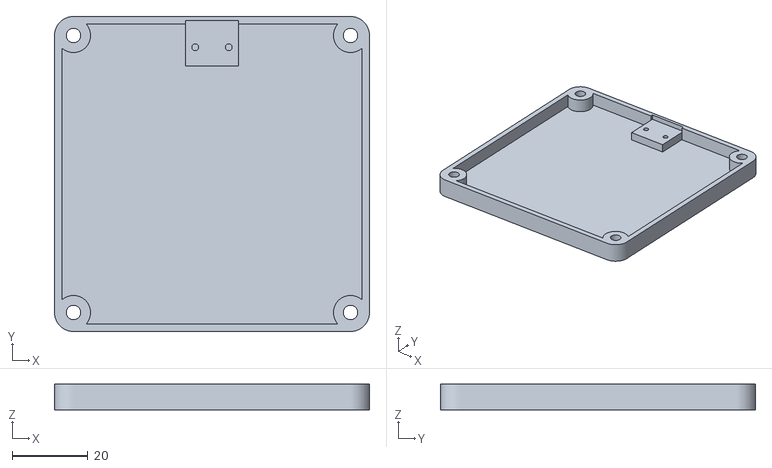
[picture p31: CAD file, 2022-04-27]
Misc/Keypad Case 3D Model/case-bottom.stl
83.0 x 83.0 x 6.80

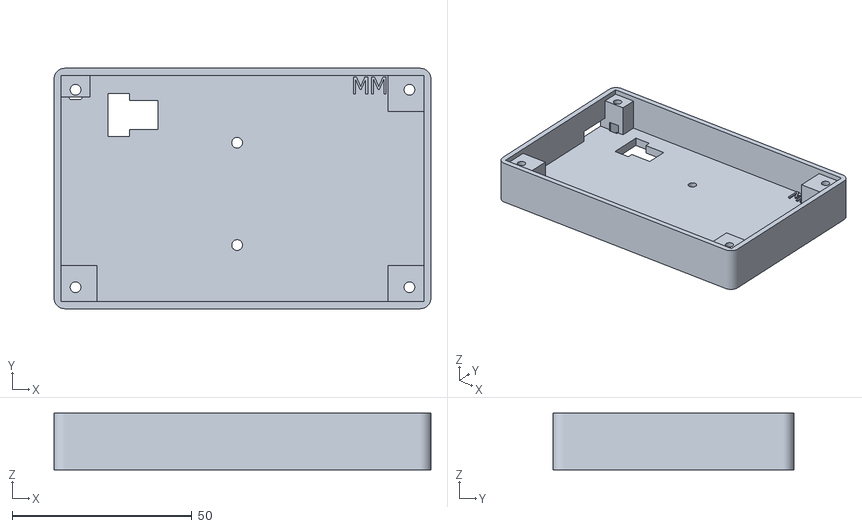
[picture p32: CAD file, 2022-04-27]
Misc/LCD Case 3D Model/20x4Case.stl
105.0 x 67.0 x 15.8

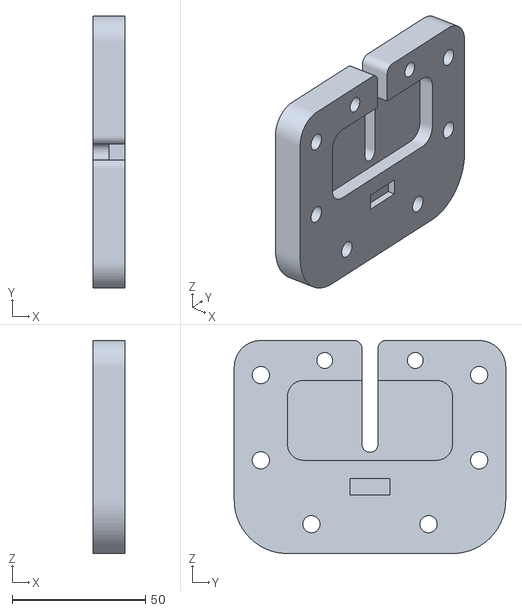
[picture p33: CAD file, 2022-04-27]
Misc/Clamp 3D Model/SpecimenHolder_OuterPart.stl
12.0 x 102.0 x 80.0

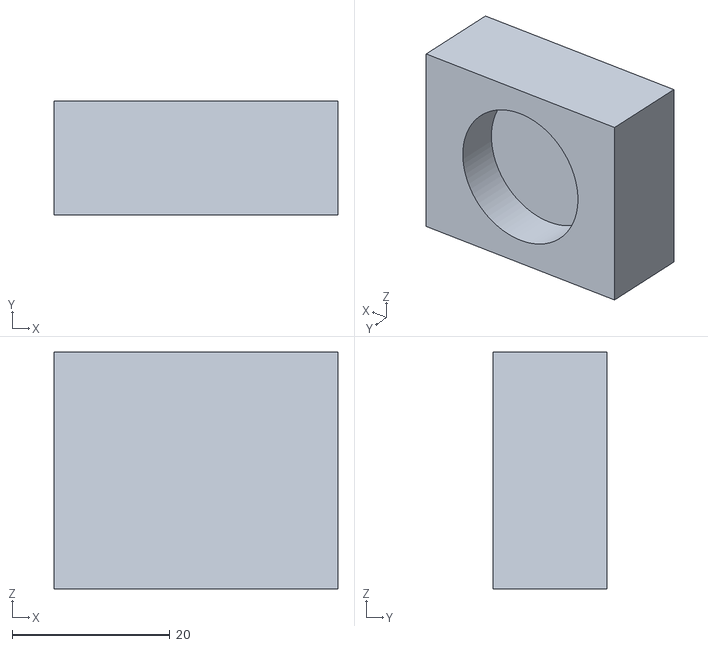
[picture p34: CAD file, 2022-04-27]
Misc/Clamp 3D Model/ClampingPlate.stl
36.0 x 14.5 x 30.0

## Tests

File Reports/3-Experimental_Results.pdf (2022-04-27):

PP-2017 V2.1

EXPERIMENTAL DESIGN | 1

# Uni-axial Automated Tensile System Experimental Results

Mazin Chater, Youssef Jalwaj Soubai, Jaden Pharoah

Activity Report

✦

### 1 RESEARCH QUESTION

A uni-axial tensile tester is a widely used system for gathering ultimate tensile strength and Young’s Modulus of a given material. Generally, these systems can be expensive and sophisticated yet their value as an educational tool for chemistry students is significant. As such, a cheaper, student-friendly design is highly desirable. Provided a minimally functional base model with issues ranging from largely inaccurate and imprecise results, obscure functionality, and generally an unpleasant and non-intuitive user interface, a targeted solution must aim to re-envision and harmonize the old structure into a more refined prototype. An effective solution is ideally considered when a low-budget, accurate and reliable system is readily accessible.

### 2 EXPERIMENTAL RESULTS

What follows is an experimental analysis of results gathered from the implementation of a friction-less, automated uni-axial system. Two distinct materials, namely nitrile and latex, were used to conduct a number of trials. Pictured in Figure 1 is a stress-strain curve from an arbitrary trial testing a latex sample. Of special

- Mazin Chater,
E-mail: mchater3@albany.edu,
- Youssef Jalwaj Soubai,
E-mail: yjalwaj-soubai@albany.edu,
- Jaden Pharoah,
E-mail: jpharoah@albany.edu
Electrical & Computer Engineering, University at Albany.

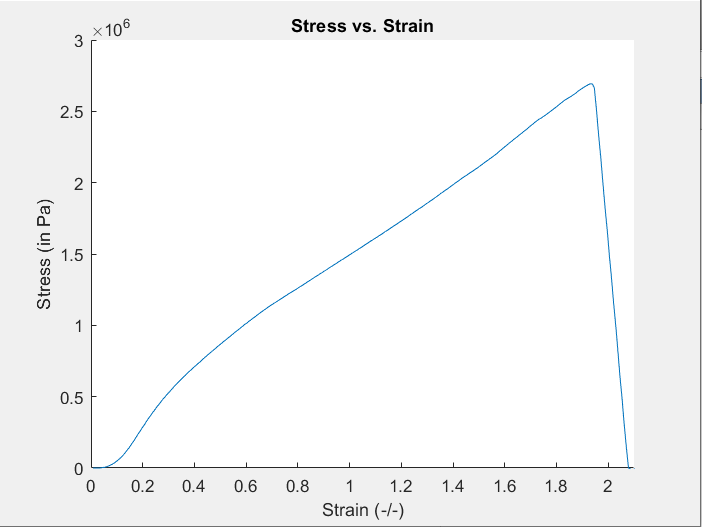
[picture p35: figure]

Figure 1. Stress-strain curve derived from our system for latex glove sample

consideration is the general uniformity of each plot. In the base model and in all other manual systems more generally, achieving a ”smooth” plot is extremely difficult due to the necessary application of a constant increase in strain. The use of an automated linear actuator to fulfill this requirement eliminates human error associated with non-uniform data collection.

### 3 DATA ANALYSIS

Table 1 summarizes experimental results from five trials conducted on nitrile and latex glove samples. Error is presented in terms of percent difference from known values. It is worth noting that the slight error arising from the latex samples is likely due to differences in glove thickness. The latex glove thickness used in

Activity Report

2 | EXPERIMENTAL DESIGN
Metric | Sample | # Trials | Our System | Known Value | Error
Young’s Modulus | Latex Glove | 5 | 770 ± 30 kPa | 740 ± 10 kPa | ±4
.. | Nitrile Glove | 5 | 2.4 ± 0.2 MPa | 2.4 ± 0.2 MPa | ±0
Ultimate Tensile Strength | Latex Glove | 5 | 2.7 ± 0.3 MPa | 3.3 ± 0.1 MPa | ±18
.. | Nitrile Glove | 5 | 4.4 ± 0.4 MPa | 4.4 ± 0.1 MPa | ±0
Table 1
Summary of experimental results from multiple trials

gathering the Table 1 results was 127 microns while the known values were achieved using a thickness of 110 microns. When accounting for this difference, there is only a marginal discrepancy in the referenced metrics. Another potential source of error is variability in material strength throughout the glove. A more rigorous assessment of the accuracy of the system should be performed with uniform materials with minimized variability. Despite these slight nuances, the general form of the stress-strain curves are nearly identical to those obtained by commercial machines, adding validity to the system in a broader sense.

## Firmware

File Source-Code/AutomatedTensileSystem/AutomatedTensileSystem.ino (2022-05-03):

// Load cell
#include <HX711_ADC.h>
#include <EEPROM.h>

// LCD
#include <Wire.h>
#include <LiquidCrystal_I2C.h>

LiquidCrystal_I2C lcd(0x27, 20, 4);

// Keypad
#include <Keypad.h>
const byte ROWS = 4; //four rows
const byte COLS = 4; //three columns
char keys[ROWS][COLS] = {
  {'1', '2', '3', 'A'},
  {'4', '5', '6', 'B'},
  {'7', '8', '9', 'C'},
  {'t', '0', '#', 'D'}
};

// Keypad mappings
byte rowPins[ROWS] = {26, 27, 28, 29}; //connect to the row pinouts of the keypad
byte colPins[COLS] = {22, 23, 24, 25}; //connect to the column pinouts of the keypad

Keypad keypad = Keypad( makeKeymap(keys), rowPins, colPins, ROWS, COLS );

char inByte;

// SD Card
#include <SD.h>
#include <SPI.h>
File myFile;
int pinCS = 53;
int counter = 0;

// Time Functionality to calculate actuator distance
unsigned long Reference_Time = 0;
unsigned long Current_Time = 0;
unsigned long Time_Difference = 0;
double Retract_Distance = 0.0;

// HX711
const int HX711_DT = 7; //mcu > HX711 dout pin
const int HX711_SCK = 6; //mcu > HX711 sck pin
HX711_ADC LoadCell(HX711_DT, HX711_SCK);
unsigned long t = 0;

// Pin mappings of motor driver
const int Extend = 5; // Extend is in 1
const int Retract = 4; //

// FSM Flags & States
int calibrateFlag = 0;
int runFlag = 0;
int stopFlag = 0;
int endCalibrateFlag = 0;

enum userActions { START, MENU, CALIBRATE, RUN };
userActions state;

///////////////////////////////////////////////////////////////////////////////////////////////////////////////////////////////////

void setup() {

  Serial.begin(9600);

  // Initialize LCD
  lcd.init();
  lcd.backlight();
  lcd.clear();

  // Load cell startup calibration
  LoadCell.begin();
  LoadCell.setReverseOutput(); //For strain
  float calibrationValue; // calibration value (see example file "Calibration.ino")
  calibrationValue = -88.16;

  // Load cell startup
  unsigned long stabilizingtime = 2000; // precision right after power-up can be improved by adding a few seconds of stabilizing time
  boolean _tare = true; //set this to false if you don't want tare to be performed in the next step
  LoadCell.start(stabilizingtime, _tare);
  if (LoadCell.getTareTimeoutFlag()) {
    Serial.println("Timeout, check MCU>HX711 wiring and pin designations");
    while (1);
  }
  else {
    LoadCell.setCalFactor(calibrationValue); // set calibration value (float)
    Serial.print('\t');
  }

  // Actuator pin setup & initialization
  pinMode(Extend, OUTPUT);
  pinMode(Retract, OUTPUT);
  digitalWrite(Extend, LOW);
  digitalWrite(Retract, LOW);

  keypad.addEventListener(keypadEvent); // Add an event listener for this keypad

  //SD Card Initialization
  pinMode(pinCS, OUTPUT);

  if (SD.begin())
  {
    Serial.println("SD card is ready to use.");
  } else
  {
    Serial.println("SD card initialization failed");
    return;
  }

}

///////////////////////////////////////////////////////////////////////////////////////////////////////////////////////////////////

// Actuator movements
void delayActuator() {
  digitalWrite(Retract, LOW);
  digitalWrite(Extend, LOW);
  delay(3000);
}

void stopActuator() {
  digitalWrite(Retract, LOW);
  digitalWrite(Extend, LOW);
}

void extendActuator() {
  digitalWrite(Retract, LOW);
  digitalWrite(Extend, HIGH);
  delay(42000);
}

void retractActuator() {
  digitalWrite(Retract, HIGH);
  digitalWrite(Extend, LOW);
}

// Prints base menu screen 
void printMenu() {
  lcd.clear();
  lcd.print("Auto Tensile Tester");
  lcd.setCursor(0, 1);
  lcd.print("------------------------");
  lcd.setCursor(0, 2);
  lcd.print("A)Calibrate");
  lcd.setCursor(0, 3);
  lcd.print("B)Run Test");
}

// Gets instantaneous data reading of load cell
double readLoadCell() {

  static boolean newDataReady = 0;
  float cell = 0;

  // Check for new data/start next conversion:
  if (LoadCell.update()) newDataReady = true;

  // get smoothed value from the dataset:
  if (newDataReady) {
    if (millis() > t) {
      cell = LoadCell.getData();
      newDataReady = 0;
      t = millis();
      delay(100);
    }
  }
  return cell;
}

// Gets keypad input
int obtainCalibrationDigit(int scale) {
  char digit = ' ';
  const int EMPTY_CHAR = 0;
  do {
    digit = keypad.getKey();
    delay(100);
    Serial.print(digit);

    int ascii = (int) digit;
    //lcd.print(ascii);
    Serial.println(ascii);
  } while (digit == EMPTY_CHAR);  //ASCII value 0 for empty character

  return (((digit - 48) * scale));
}

///////////////////////////////////////////////////////////////////////////////////////////////////////////////////////////////////

void calibrate() {

  Serial.println("Start calibration:");
  Serial.println("Send 't' from serial monitor to set the tare offset.");

  retractActuator();
  lcd.clear();
  lcd.print("CALIBRATE STATE");
  lcd.setCursor(0, 1);
  lcd.print("--------------------");
  lcd.setCursor(0, 2);
  lcd.print("Wait 10 seconds for");
  lcd.setCursor(0, 3);
  lcd.print("retraction period.");
  delay(15000);
  stopActuator();

  lcd.clear();
  lcd.print("CALIBRATE STATE");
  lcd.setCursor(0, 1);
  lcd.print("--------------------");
  lcd.setCursor(0, 2);
  lcd.print("Press '*' to set");
  lcd.setCursor(0, 3);
  lcd.print("the tare offset.");

  boolean _resume = false;
  while (_resume == false) {

    LoadCell.update();
    Serial.println("Infinite Loop");

    inByte = keypad.getKey();
    int ascii = (int) inByte;
    Serial.println(inByte);
    if (inByte == 't') {
      LoadCell.tareNoDelay();
    }
    if (LoadCell.getTareStatus() == true) {
      _resume = true;
    }

    delay(100);
  }

  Serial.println("Place known mass on load cell");
  Serial.println("Enter known mass (g):");

  lcd.clear();
  lcd.print("Place known mass");
  lcd.setCursor(0, 2);
  lcd.print("Enter known mass (g)");
  lcd.setCursor(0, 3);
  lcd.print("Using four digits");

  float known_mass = 0;
  _resume = false;

  while (_resume == false) {

    Serial.println("Infinite Loop2");

    LoadCell.update();
    delay(100);

    int sum = obtainCalibrationDigit(1000);
    sum = sum + obtainCalibrationDigit(100);
    sum = sum + obtainCalibrationDigit(10);
    sum = sum + obtainCalibrationDigit(1);
    known_mass = sum;

    Serial.println("KNOWN_MASS: ");
    Serial.println(known_mass);

    if (known_mass != 0) {
      Serial.print("Known mass is: ");
      Serial.println(known_mass);
      _resume = true;
    }
  }

  lcd.clear();
  lcd.setCursor(0, 2);
  lcd.print("User Input: ");
  lcd.print(known_mass);

  delay(1000);

  LoadCell.refreshDataSet(); //refresh the dataset to be sure that the known mass is measured correct
  float newCalibrationValue = (-1) * LoadCell.getNewCalibration(known_mass); //get the new calibration value
  LoadCell.setCalFactor(newCalibrationValue);

  lcd.clear();

  Serial.print("New calibration value has been set to: ");

  lcd.print("New calibration set to: ");
  lcd.setCursor(0, 2);
  lcd.print(newCalibrationValue);
  Serial.print("new calibration set to: ");
  Serial.println(newCalibrationValue);
  delay(2000);
  lcd.clear();
  lcd.setCursor(0, 1);
  lcd.print("End of calibration");

  lcd.setCursor(0, 2);
  lcd.print("Remove Mass!");
  delay(3000);

  digitalWrite(Retract, LOW);
  digitalWrite(Extend, HIGH);
  delay(15000);
  stopActuator();

  Serial.println(newCalibrationValue);
  Serial.println("End calibration");

}

///////////////////////////////////////////////////////////////////////////////////////////////////////////////////////////////////

void loop() {

  double loadcell = 0;

  if (runFlag == 1) {
    loadcell = readLoadCell();
    Current_Time = millis();
    Time_Difference = (Current_Time - Reference_Time);
    Retract_Distance = ( (double) Time_Difference) * (0.000659); //rate = 30cm/46,000 milliseconds

    Serial.print(loadcell);
    Serial.print('\t');
    Serial.print(Retract_Distance);
    Serial.print('\n');


    //SD Card
    // if the file opened okay, write to it:
    if (myFile) {
      myFile.print(loadcell);
      myFile.print('\t');
      myFile.print(Retract_Distance);
      myFile.print('\n');
    }
    // if the file didn't open, print an error:
    else {
      Serial.println("error opening test.txt");
      lcd.clear();
      lcd.setCursor(0, 1);
      lcd.print("Error opening file");
      lcd.setCursor(0, 2);
      lcd.print("for SD Card");
      lcd.setCursor(0, 3);
      lcd.print("Press 'c' to stop");

    }

    if (inByte == 's') {
      Serial.println("-----------STOP FLAG-----------");
      lcd.clear();
      lcd.print("STOP INITIATED");
      lcd.setCursor(0, 1);
      lcd.print("--------------------");
      lcd.setCursor(0, 2);
      lcd.print("Extending back to");
      lcd.setCursor(0, 3);
      lcd.print("starting position.");
      stopFlag = 1;
    }
  }

  else if (calibrateFlag == 1) {
    calibrate();
    endCalibrateFlag = 1;
  }


  FSM();

  //Poll KeyPad
  char key = keypad.getKey();
  Serial.print("key: ");
  Serial.println(key);
  //delay(100);

}

///////////////////////////////////////////////////////////////////////////////////////////////////////////////////////////////////

void FSM() {

  // Transitions
  switch (state) {
    case START:
      printMenu();
      state = MENU;
      break;

    case MENU:

      delay(100);


      if (inByte == 'r') {
        Serial.println("RUN STATE");

        lcd.clear();
        lcd.print("RUN STATE");
        lcd.setCursor(0, 1);
        lcd.print("--------------------");
        lcd.setCursor(0, 2);
        lcd.print("Press 'c' to stop");
        lcd.setCursor(0, 3);
        lcd.print("when break occurs.");
        lcd.setCursor(0, 4);

        delayActuator();
        retractActuator();
        
        // Create/Open file
     
        char filename[32] = "test";
        char cntStr[16];
        itoa(counter, cntStr, 10);
        counter++;
        strcat(filename, cntStr);
        strcat(filename, ".txt");
        
        myFile = SD.open(filename, FILE_WRITE);
        Reference_Time = millis(); //Obtain Time when run starts
        state = RUN;
        Serial.println("State is run");
      }
      else if (inByte == 'c') {
        state = CALIBRATE;
      }
      else {
        // If no state change
        state = MENU;
      }
      break;

    case CALIBRATE:
      if (endCalibrateFlag == 1) {
        endCalibrateFlag = 0;
        calibrateFlag = 0;

        printMenu();

        state = MENU;
      }
      break;

    case RUN:
      // If test is concluded
      if (stopFlag == 1) {
        stopFlag = 0;
        runFlag = 0;
        myFile.close(); // close the file for SD card
        delayActuator(); // Stops the actuator and waits 3s
        extendActuator(); // Extends back to bottom position
        stopActuator(); // Stops actuator

        printMenu();

        state = MENU;
      }
      // If no state change
      else {
        state = RUN;
      }
      break;

  }

  // Actions
  switch (state) {
    case START:
      break;

    case MENU:
      break;

    case CALIBRATE:
      calibrateFlag = 1;
      break;

    case RUN:
      runFlag = 1;
      break;
  }
}


// Taking care of some special events.
void keypadEvent(KeypadEvent key) {
  //Serial.println("INSIDE keyPad Event");
  switch (keypad.getState()) {
    case PRESSED:
      if (key == 'A') {
        inByte = 'c';
      }
      if (key == 'B') {
        inByte = 'r';
      }
      if (key == 'C') {
        inByte = 's';
      }
      if (key == '*') {
        inByte = 't';
      }
      break;
  }
}
